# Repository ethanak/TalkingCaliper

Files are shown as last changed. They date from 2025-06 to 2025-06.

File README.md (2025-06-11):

# TalkingCaliper

A multilingual speaking caliper attachment.

## Short description

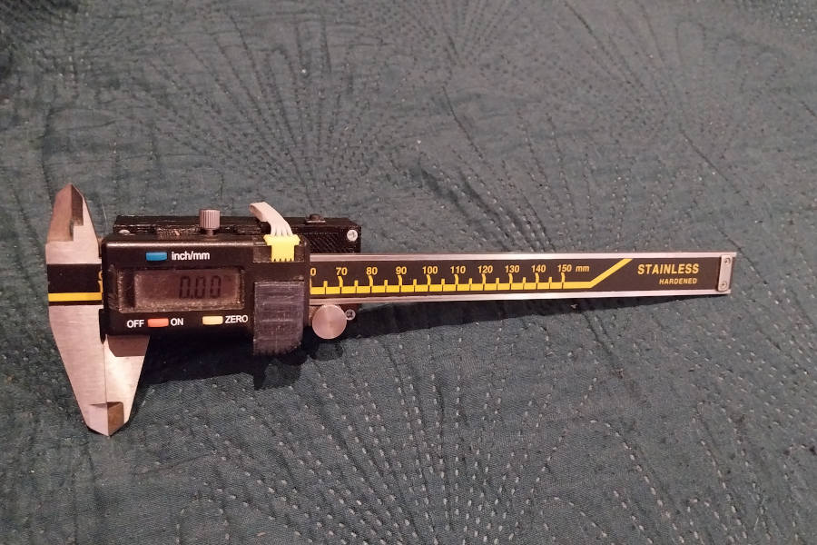
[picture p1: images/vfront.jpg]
general view


Short movie: [YouTube video](https://youtu.be/fLb1sWjNS7g)

The device is an attachment for the popular Vorel caliper, it can also be used in all measuring devices of this company with a compatible interface (tire tread depth gauge, dial gauge, etc.). In the case of the caliper, it is mounted on the rear wall of the housing in a way that does not interfere with its normal use.

The attachment allows for convenient use of the caliper;

* by blind and visually impaired people
* in poor lighting conditions
* in situations where observing the display is difficult or impossible

In contrast to previous designs using the full TTS mechanism (and thus limited to one specific language), a corpus synthesizer was used here. Due to the relatively small number of messages, it is possible to pre-record them in virtually any language. The program code allows you to select (during compilation) one of four languages:

* English (RHVoice, two voices bdl and slt);
* Polish (RHVoice, two voices magda and natan)
* Spanish (RHVoice, one voice mateo)
* German (Piper-TTS, one voice thorsten)

It is also possible to use an Android phone and use the phone's built-in TTS system, but it is not very convenient (especially for the first group of users)

The device can work in the following modes:

* continuous reading - current measurement results are provided with a one-second break
* reading changes - only measurement results are provided if the value has changed or a reading has been forced.
* reading on demand - after pressing a key.

The units (millimeters or inches) depend on the settings of the caliper itself. Each first reading ends with the unit being provided, the next ones are the same numbers. Since the result in millimeters always contains two decimal digits, in inches three, the reading is always unambiguous. Additionally, it is possible to set the reading option in thousandths of an inch for results below one inch (the unit is mil), in order to shorten the voice message without losing its intelligibility.

## Operation

The device has only one button. The options are as follows

* single click - in the change reading mode or on demand, it reads the current result;
* hold - changes the reading mode;
* double click - reads the battery status;
* click and hold - enters the settings mode.

In the settings mode:

* single click - change value
* hold - exit the settings mode without saving and return to the previous settings
* double click - change the parameter
* click and hold - save.

The following parameters can be set:

* speech speed (seven options, from absurdly slow to very fast);
* volume (three options);
* voice (only if there is more than one);
* way of reading small values;
* separation of digits when reading.

Additionally, after connecting the charger, the charging mode is started, where the device does not say anything. You can exit it by holding the key.

## Program

The program is currently only adapted to the XIAO ESP32S3 board.
Used in program:

* sonic_lite from library [Sonic](https://github.com/waywardgeek/sonic/)
* Piece of code for reading caliper data from  [EspDRO](https://github.com/MGX3D/EspDRO)

### Requirements:

* Arduino IDE with ESP32 Board version 3.1 or later installed
* ESP8266Audio library installed

### IDE settings:

- Selected board: XIAO ESP32-S3
- CPU Frequency: 80 MHz
- Partition Scheme: Maximum APP (7.9 MB APP, No OTA/No FS)

### Program settings:

In the common.h file:

```c
//Uncomment if you don't have/don't need the BlueTooth application
//#DISABLE_BLE

//Uncomment if you don't need charging control
//#DISABLE_CHARGER
```

In the i18n.h file:

```c

//Uncomment for language Polish
//#define VOICE_IS_PL
```

All other VOICE_IS definitions should be commented out.

For other languages:

* for English comment out all VOICE_IS definitions
* for others uncomment only the appropriate definition.

## Electronics

### Required elements

* XIAO ESP32-S3
* MAX98357A module
* Small speaker (originally used 15x24x4 1W)
* LiPo battery min. 250 mAh
* 2 x Schottky diode (min. 0.5A)
* 2 x rectifier diode (the smallest, any parameters) to power the caliper
* tact switch button
* small power switch
* resistors, capacitors, mounting elements according to the diagram

### Test version

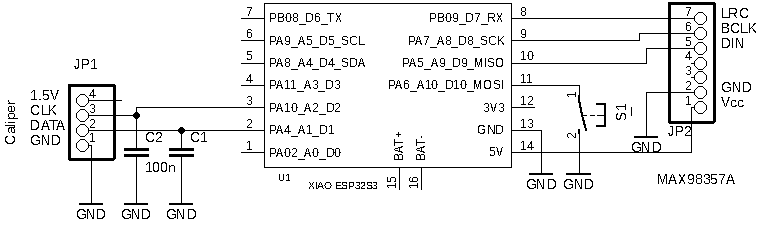
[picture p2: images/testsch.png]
simplified version diagram


This version is used only to test the program's cooperation with the caliper. It requires only three additional components beyond the main Xiao board and the amplifier (two capacitors and a button), but can be used both to evaluate the usability of the program and to work on introducing a new voice or language. The circuit can be assembled on a small (170 holes) breadboard.

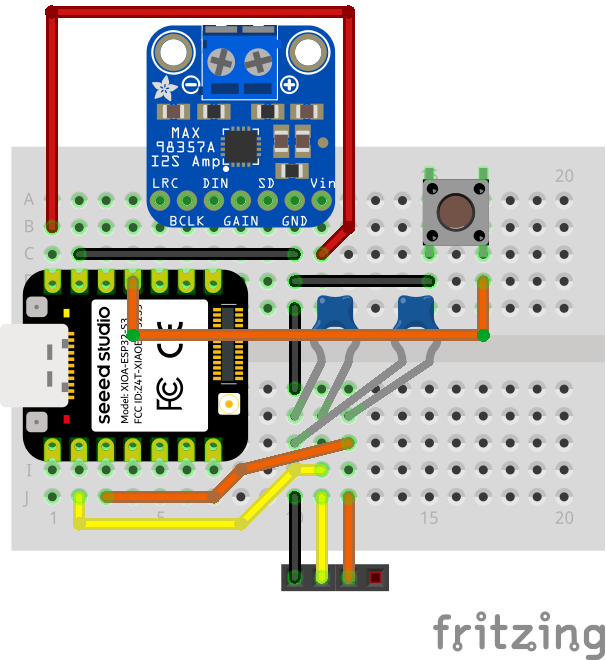
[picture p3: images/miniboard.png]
example breadboard layout


In this version, the caliper must be powered by an internal battery. When compiling, uncomment

```c
#DISABLE_CHARGER
```

in the common.h file so that the program does not try to check the charger connection to a non-existent battery.

Since there is no battery, the command to check the battery status will generate incorrect readings, but the rest will work.

### Base version

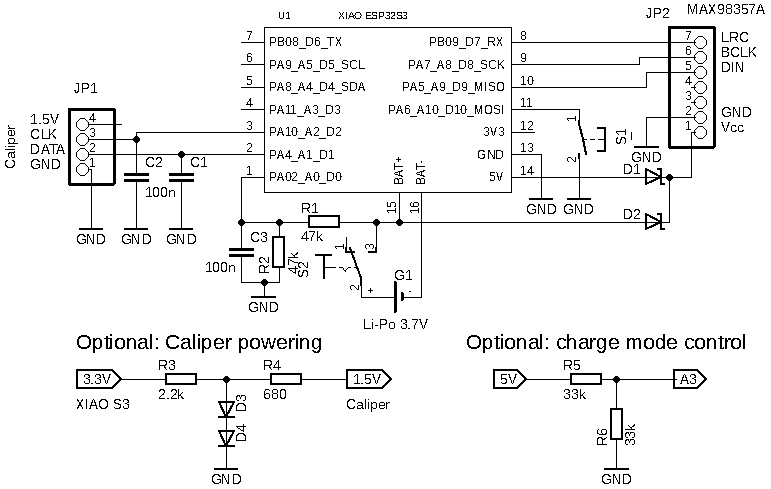
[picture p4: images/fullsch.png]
full version diagram


The simplest one that is realistically possible to make a working device. It differs from the previous one in that the amplifier power is taken either directly from the battery or (in the case of a USB connection) from the Vin input. Additionally, a battery status meter is already connected.

As before, the charger connection detection must be disabled.

Additional elements: two Schottky diodes, two resistors, optional capacitor.

Instead of Schottky diodes, you can use rectifier diodes of min. 0.5A as a last resort,
but you have to take into account that the voltage supplying the I2S amplifier circuit
may drop below the minimum required value of 2.5V with a partially discharged battery.

### Caliper power supply from the attachment battery

If the attachment is not permanently attached to the caliper, this should not be used and the caliper should be powered from the internal battery. In the case of a permanent connection, this should be considered: as a rule, the time needed to recharge the battery is at least an order of magnitude shorter than the time needed to find a battery store and buy one. And as we know, batteries discharge at the least expected moment... In addition, the system (including the caliper) can then be powered by any charger (if the battery is discharged).

Cost: two rectifier diodes, two resistors, connecting all four wires to the caliper plug. Additionally, approx. 1 mA of current draw from the battery.

It should be impossible to insert a battery into the caliper!

### Charging sensor

Allows the device to automatically switch to silent mode (it is not advisable for the device to talk during charging).

Cost: two resistors.

Comment required

```c
#DISABLE_CHARGER
```

in common.h file

### Notes

To calibrate the battery status sensor, access to gnd and the +bat pad is required. While this is trivial before installing the attachment (+bat is available on the switch leads, gnd in several places) - after installation, this is no longer possible. Remember this and calibrate before permanently installing the attachment.

## Mechanical design

### Caliper plug

The project is a modified version of the plug from [EspDRO](https://github.com/MGX3D/EspDRO).
You can also use the original version.

The plug should be printed from TPU or similar elastomer [STL file](/connector/mini_connector.jpg),
preferably with a 0.1 mm layer. The way to attach the cable is shown in the pictures in the [Connector](/connector/) folder.

### Housing

Due to the possibility of using different elements and configurations, it is not possible to include STL files. The attached file [OpenSCAD](/caliper.scad) can be a basis for designing the housing

## Other voices and languages.

It is possible to implement other voices (e.g. using commercial
synthesizers), as well as other languages. More information in the folder
[voice preparation](/prepare).

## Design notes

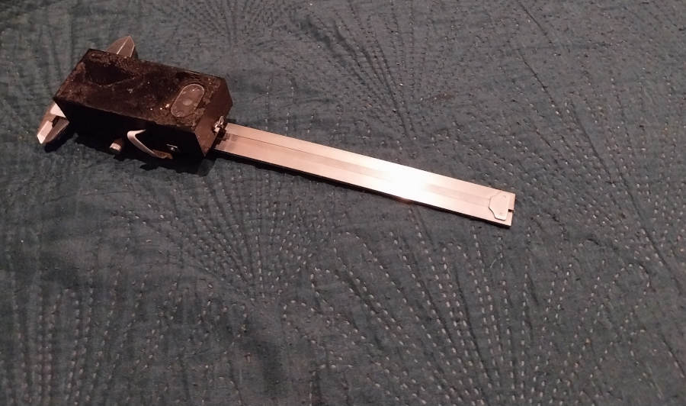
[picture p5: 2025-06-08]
images/vback.jpg

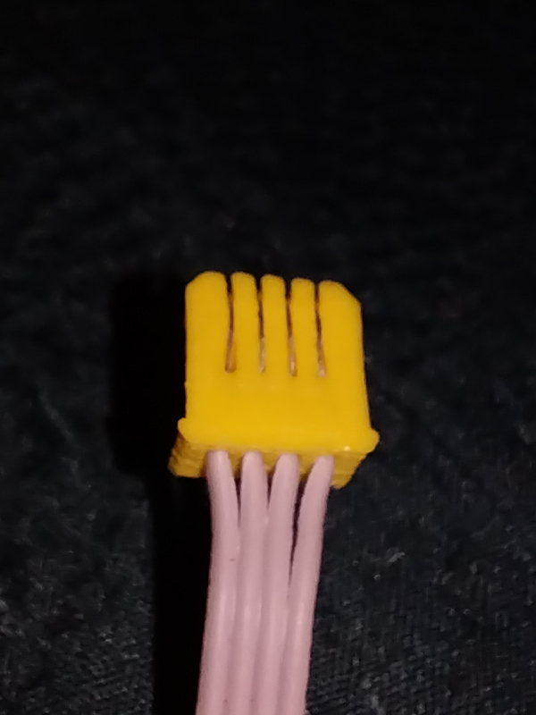
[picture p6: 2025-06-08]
connector/connb.jpg

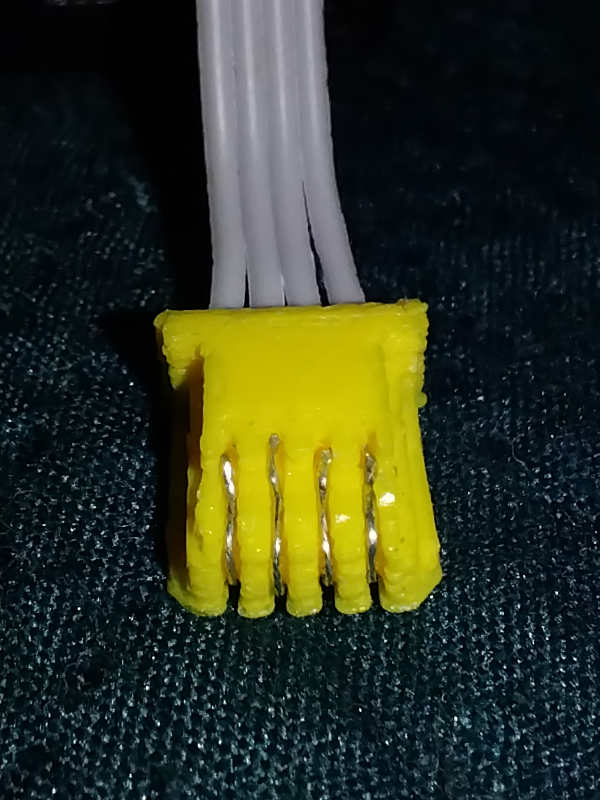
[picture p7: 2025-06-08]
connector/connf.jpg

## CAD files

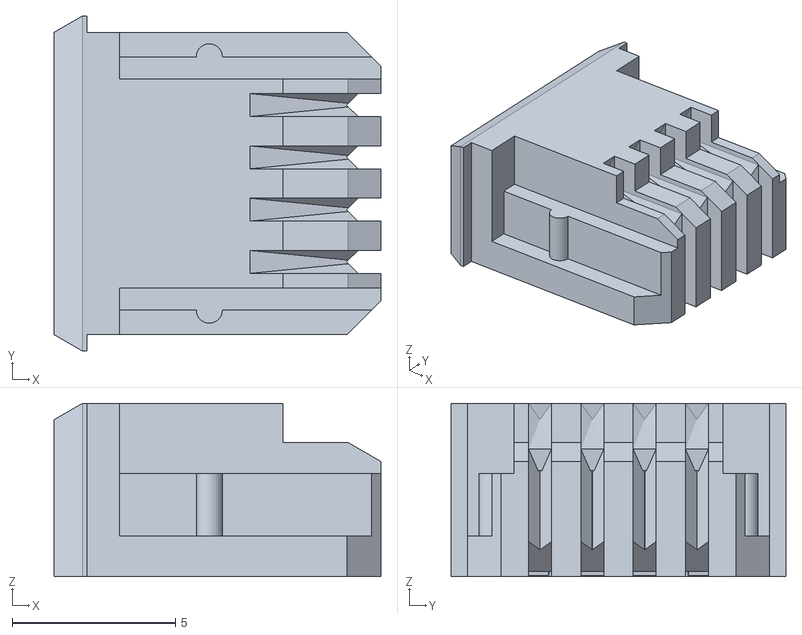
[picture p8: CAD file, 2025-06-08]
connector/mini_connector.stl
10.0 x 10.2 x 5.30

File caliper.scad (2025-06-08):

// what will be printed?
whatprint = 0; // [0:cover, 1: pokrywka, 2: speaker holder, 3: pcb holder]

module symetric(n=0)
{
    for (symetri3s = [0,1]) mirror([
        (n==0) ? symetri3s : 0,
        (n==1) ? symetri3s : 0,
        (n==2) ? symetri3s : 0]) children();
}
module icube(x,y,z)
{
    translate([-x/2, -y/2, 0]) cube([x,y,z]);
}

$fn=32;


// speaker dimensions
mi_d=15.8;
mi_l=24.8;
mi_h=4;
mi_left= mi_d/2+2;



wall = 1.6;
mainlen_ex = 75;
mainlen_in = mainlen_ex-2*wall;
mainwid_in = 30;
mainwid_ex=mainwid_in + 2*wall;
mainh_in = 17.4;
botom=2.1;
gtop=1.5;

// pcb holes
hdx=8*2.54;
hdy=10*2.54;
hlx=18.5+2*2.54;

pip1=[[12,24]];
pip2=[[12,12],[35,7]];

xkey=59;
wkey=6.4;
wswitch = 9.6;
piph=9;

module topik()
{
    translate([-wall,0,mainh_in+1]) difference()
    {
        union() {
            translate([0,-mainwid_ex/2,0]) cube([mainlen_ex,mainwid_ex,gtop]);
            translate([mainlen_in+wall,-wswitch/2+0.6,-2.4]) cube([wall,wswitch-1.2,2.5]);
            translate([pip2[1][0]+pip2[1][1]+0.4,mainwid_in/2,-6]) cube([7.2,wall,6.1]);
        }
        for (p=pip2) translate([p[0]-0.6,mainwid_in/2-1,-1]) cube([p[1]+1.2,5,5]);
        mirror([0,1,0]) translate([pip1[0][0]-0.6,mainwid_in/2-1,-1]) cube([pip1[0][1]+1.2,6,6]);
        for (x = [3, mainlen_ex-3]) symetric(1) {
            translate([x,mainwid_ex/2-3,-1]) {
                cylinder(d=2.4,h=10);
                translate([0,0,gtop-0.2]) cylinder(d1=2.5, d2=6.5, h=2);
            }
        }
    }
}
module spikiper()
{
    difference() {
        translate([-mi_left,-13.5,0]) cube([mi_left*2-2,27,1.3]);
        symetric(1) translate([mi_left-2-5,13.5-4,-1]) cube(6);
    symetric(1) translate([-mi_left+3,mainwid_in/2-3,-1]) cylinder(d=2.4,10);
        translate([0,0,-5]) hull() symetric(1) translate([0,(mi_l-mi_d)/2,0]) cylinder(d=mi_d-6,h=10);
    }
    icube(mi_left*2-5,6,0.9);
    cylinder(d=6,h=0.9+1.2);

}

module buda()
{
    module boks(h)
    {
        difference() {
            translate([-wall,-mainwid_ex/2,-botom]) cube([mainlen_ex,mainwid_ex,botom+h]);
            translate([0,-mainwid_in/2,0]) 
                cube([mainlen_in,mainwid_in, h+1]);
        }
    }
    
    module hole(ha)
    {
        hb=ha+2.1-0.9;
        cylinder(d=1.8,h=hb+1);
        cylinder(d=2.4,h=2);
        translate([0,0,hb-0.4]) cylinder(d1=1.8,d2=2.4,h=0.6);
    }
    
    difference() {
        union() {
            boks(mainh_in);
            // głośnik
            translate([mainlen_in-2*mi_left,-mainwid_in/2,-2.1+0.9]) cube([20.1,mainwid_in,1+mi_h]); 
            
            // dystans pod płytkę
            for (x=[hlx,hlx+hdx]) symetric(1) translate([x,hdy/2,-0.1]) {
                cylinder(d=4.5, h=2.1);
                translate([-4.5/2,0,0]) cube([4.5,3.5,2.1]);
            }
            // skrzydełka
            for (p=pip2) translate([p[0]-wall,mainwid_in/2,0]) cube([p[1],wall,mainh_in+piph]);
            for (p=pip1) translate([p[0]-wall,-mainwid_ex/2,0]) cube([p[1],wall,mainh_in+piph]);
             // mocowania topu prawe
            symetric(1) translate([mainlen_in+wall-6,mainwid_ex/2-6,mainh_in-5]) hull() {
                cube([5.5,5.5,5]);
                translate([5,5,-5]) cube(0.5);
            }
            // mocowania topu lewe
            symetric(1) translate([-wall,mainwid_ex/2-6,mainh_in-5]) hull() {
                cube([6,6,5]);
                translate([0,5,-5]) cube(0.5);
            }
            
            // klawisz
            translate([xkey-wkey/2-4.1,mainwid_in/2-3.6,mainh_in-wkey]) hull() {
                cube([wkey+8.2,4,wkey-1]);
                translate([4,4,-4]) cube([wkey+2,0.1,0.1]);
            }
            // wyłącznik
            *translate([-wall,-wswitch/2-4.1,mainh_in-6.8]) cube([wall+2+1.6,wswitch+8.4,6]);
            translate([mainlen_in-3.5,-wswitch/2-4.2,mainh_in-6.8]) {
                hull() {
                    cube([4,wswitch+8.4,6]);
                    translate([3.6,4,-4]) cube([0.4,wswitch+0.4,1]);
                }
            }
        }
        
        // śruby topu
        for (x = [3, mainlen_ex-3]) symetric(1) {
            translate([x-wall,mainwid_ex/2-3,mainh_in-6]) {
                cylinder(d=1.8,h=10);
                cylinder(d=2.4,h=3);
            }
        }
        // otwór na kabel
        translate([pip2[1][0]+pip2[1][1]-wall,mainwid_in/2-1,6]) cube([8,8,20]);
        // otwór na głośnik
        translate([mainlen_in-mi_left,0,-5]) hull() symetric(1) translate([0,(mi_l-mi_d)/2,0]) cylinder(d=mi_d-4,h=7);
        translate([mainlen_in-mi_left,0,-2.1+0.9]) hull() symetric(1) translate([0,(mi_l-mi_d)/2,0]) cylinder(d=mi_d+0.8,h=7);
        
        // otwory na mocowanie głośnika    
        translate([mainlen_in-mi_left,0,-2.1+0.9]) symetric(1) translate([-mi_left+3,mainwid_in/2-3]) hole(mi_h-2.1+0.9);
        // otwory na mocowanie płytki
        for (x=[hlx,hlx+hdx]) symetric(1) translate([x,hdy/2,-2.1+0.9]) hole(2);
        // usb
        translate([-wall-1,-6,4.4]) cube([wall+2,12,5]);
        // klawisz
        translate([xkey-wkey/2,mainwid_in/2-5,mainh_in-wkey]) cube([wkey,8,wkey+1]);
        translate([xkey-wkey/2-2.5,mainwid_in/2-2,mainh_in-wkey]) cube([wkey+5,2,wkey+1]);
        // wyłącznik
        *translate([-wall-1,-wswitch/2,mainh_in-6]) cube([wall+8,wswitch,7.5]);
        *translate([0,-wswitch/2-2.5,mainh_in-7]) cube([2,wswitch+5,8]);
        
        translate([mainlen_in-5,-wswitch/2,mainh_in-6]) cube([wall+8,wswitch,7.5]);
        translate([mainlen_in-2,-wswitch/2-2.5,mainh_in-7]) cube([2,wswitch+5,8]);
    }
}

hprz=5;
module przekladka()
{
    translate([0,0,0.9+hprz+3.6]) mirror([0,0,1]) difference()
    {
        union() {
            translate([20,-mainwid_in/2+1,0]) cube([hlx+hdx-16,mainwid_in -2, 0.9]);
            intersection() {
                for (x=[hlx,hlx+hdx]) symetric(1) translate([x,hdy/2,-0.1]) cylinder(d=4.5, h=0.9+hprz);
                translate([0,-mainwid_in/2+1,0]) cube([hlx+hdx+2,mainwid_in -2, 22.9]);
            }
        }
        translate([hdx+hlx-2.5,-10,-1]) cube([10,20,10]);
        symetric(1) translate([hlx+3,-mainwid_in/2,-1]) cube([hdx-8,6,4]);
        for (x=[hlx,hlx+hdx]) symetric(1) translate([x,hdy/2,-1]) {
            cylinder(d=2.4, h=9.1);
            cylinder(d1=6.4, d2=2.4,h=2);
        }
        // really?
        translate([0,-mainwid_in/2,-1]) cube([hdx+8,6,24]);
    }
}

if (whatprint == 0) buda();
else if (whatprint == 1) topik();
else if (whatprint == 3) przekladka();
else if (whatprint == 2) spikiper();

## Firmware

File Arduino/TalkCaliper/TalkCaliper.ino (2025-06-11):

/*
   Copyright 2025 Bohdan R, Rau <ethanak@polip.com>

   Licensed under the Apache License, Version 2.0 (the "License");
   you may not use this file except in compliance with the License.
   You may obtain a copy of the License at

     http://www.apache.org/licenses/LICENSE-2.0

   Unless required by applicable law or agreed to in writing, software
   distributed under the License is distributed on an "AS IS" BASIS,
   WITHOUT WARRANTIES OR CONDITIONS OF ANY KIND, either express or implied.
   See the License for the specific language governing permissions and
   limitations under the License.
*/
#ifndef DISABLE_BLE
#include <WiFi.h>
#endif
#include <stdarg.h>
#include <driver/adc.h>
#include <esp_adc_cal.h>
#include "i18nstrings.h"
#include VOXDEFS
#include "common.h"
//#include "soc/rtc_wdt.h"

esp_adc_cal_characteristics_t db11_chars;


uint8_t lastInch=0xff;
uint32_t lastRead;
uint32_t lastSpoken;
uint8_t mainSpeed=0;
uint8_t mainVox=0;
uint8_t mainVol=0;
uint8_t lpfilter = 0;
static bool chargeMode, lastChargeMode;
static uint8_t chargeCnt;
static uint32_t lastChargeTimer = 0;
uint16_t calibV1, calibV2;
#ifndef DISABLE_BLE
char blename[32];
bool autoBLE;
#endif

enum {
    RDM_STILL = 0,
    RDM_CHAN,
    RDM_REQ,
    RDM_CHARGE,
    RDM_MAX
};

enum {
    MAMO_STD = 0,
    MAMO_PFS
};

#ifdef MOVIE_MODE
enum {
#if VOICE_COUNT > 1
    PFMO_VOX = 0,
#endif
    PFMO_OVER,
    PFMO_TEMPO,
    PFMO_VOL,
    PFMO_MILS,
#ifndef DISABLE_MELODY
    PFMO_MELO,
#endif
    PFMO_MAX
};

#else
enum {
    PFMO_TEMPO = 0,
    PFMO_VOL,
#if VOICE_COUNT > 1
    PFMO_VOX,
#endif
    PFMO_MILS,
#ifndef DISABLE_MELODY
    PFMO_MELO,
#endif
    PFMO_OVER,
    PFMO_MAX
};

#endif


const uint8_t readModeSpk[] = {
    vword_xsstil,
    vword_xschan,
    vword_xsrequ,
    vword_xcharge
};

const char * const readModeTxt[] = {
    STR_RDSTIL,
    STR_RDCHAN,
    STR_RDREQU,
    STR_RDCHRG
};

int wordBuffer[32],wordBufLen;
char blubuffer[256];
uint8_t readMode = RDM_STILL;
uint8_t mainMode = MAMO_STD;
uint8_t pfsMode = 0;
bool enableMelody, disablePauses, enableMils;
static bool tmpMelody, tmpPauses, tmpMils;


extern void speakLocal(int cnt, const char *txt=NULL);

#if defined(DISABLE_CHARGER)
#define chargerConnected 0
#else

#ifdef DIGITAL_VIN_PIN
#define chargerConnected digitalRead(VIN_PIN)
#else
#define chargerConnected (adc1_get_raw(VIN_CHANNEL) > 500)
#endif

#endif

void setup(void)
{
    Serial.begin(115200);
    setCpuFrequencyMhz(80);

#ifndef DISABLE_BLE
    WiFi.mode(WIFI_MODE_NULL);
#endif
    adc1_config_width(ADC_WIDTH_BIT_12);
#ifdef DIGITAL_VIN_PIN
    pinMode(VIN_PIN,INPUT);
#else
    adc1_config_channel_atten(VIN_CHANNEL,ADC_ATTEN_DB_11);
#endif
    adc1_config_channel_atten(VOLT_CHANNEL,ADC_ATTEN_DB_11);
    adc1_config_channel_atten(CLK_CHANNEL,ADC_ATTEN_DB_6);
    adc1_config_channel_atten(DATA_CHANNEL,ADC_ATTEN_DB_6);
    esp_adc_cal_characterize(
        ADC_UNIT_1, ADC_ATTEN_DB_11, ADC_WIDTH_BIT_12,
        1100, &db11_chars);
    initPrefs();
    revertPrefs();
    //getCalibData();
    pinMode(KEY_PIN, INPUT_PULLUP);
#ifndef DISABLE_BLE
    delay(100);
    if (autoBLE) useBLE = true;
    else if (!digitalRead(KEY_PIN)) {
        delay(100);
        if (!digitalRead(KEY_PIN)) useBLE=true;
    }
#endif
    startSecondTask();
    delay(10);
    chargeMode = chargerConnected;
    readMode=(chargeMode) ? RDM_CHARGE : RDM_STILL;
    chargeCnt = 0;
    
    //initKey();
#ifndef DISABLE_BLE
    if (useBLE) {
        wordBuffer[0] = vword_xblu;
        wordBuffer[1] = readModeSpk[readMode];
        speakLocal(2);
    }
    else
#endif
     {
        wordBuffer[0] = readModeSpk[readMode];
        speakLocal(1);
    }
    lastChargeMode = chargeMode;
    lastRead=millis();
    lastChargeTimer = millis();
}

static uint32_t _readBattery()
{
    static uint32_t batsum=0;
    static uint8_t batstep=0;
    static uint32_t batmillis = 0;
    uint32_t curvolt;
    if (millis() - batmillis < 50) return 0;
    batmillis = millis();
    if (esp_adc_cal_get_voltage(ADC_CHANNEL_0,&db11_chars,&curvolt) != ESP_OK) return 0;
    if (batstep == 0) batsum = 0;
    batsum += curvolt;
    batstep = (batstep + 1) & 15;
    if (batstep == 0) return batsum / 16;
    return 0;
    
}

int batvolt = 0;

void readBattery()
{
    int t = _readBattery();
    if (t) batvolt = t;
}

void getStrResult(char *buf, long packet)
{
    static const char *units[]={
        " mm"," in"," ms"};
        
    long data = packet & 0xFFFFF;
    char *cb=buf;
    uint8_t neg = (packet & 0x100000) ? 1 : 0;
    uint8_t inch;
    if (packet & 0x800000) {
        data = data/2;
        inch = (enableMils && data < 1000) ? 2: 1;
        
    }
    else inch=0;
    if (neg) {
        strcpy(buf,"- ");
        buf+=2;
    }
    if (inch == 2) sprintf(buf,"%d ms", data);
    else {
        if (inch) sprintf(buf,"%d . %03d", data/1000, data%1000);
        else sprintf(buf,"%d . %02d", data/100, data%100);
        if (lastInch != inch) {
            strcat(buf, units[inch]);
        }
    }
    lastInch = inch;
}


uint32_t pfsTimer;
uint8_t tmpSpeed, tmpVox, tmpVol;
bool speaking = false;
void speakLocal(int cnt, const char *txt)
{
    qSay(mainVox, mainSpeed, mainVol, cnt, wordBuffer,txt);
    speaking = true;
}

static void vspeakTmp(int cnt, ...)
{
    int i;
    va_list ap;
    va_start(ap, cnt);
    for (i=0;i<cnt;i++) wordBuffer[i] = va_arg(ap, int);
    va_end(ap);
    qSay(tmpVox, tmpSpeed, tmpVol, cnt, wordBuffer);
    speaking = true;
}    

void announceRDM(void)
{
    wordBuffer[0] = readModeSpk[readMode];
    speakLocal(1,readModeTxt[readMode]);
}

void announcePfs(void)
{
    switch (pfsMode) {
        case PFMO_TEMPO:
        vspeakTmp(2, vword_xspeedp, (tmpSpeed+1) * NUMSTEP);
        break;

        case PFMO_VOL:
        vspeakTmp(1, vword_xvol0+tmpVol);
        break;

#if VOICE_COUNT > 1
        case PFMO_VOX:
        vspeakTmp(2,vword_xvtypp,vword_xvox);
        break;
#endif

        case PFMO_MILS:
        vspeakTmp(1, enableMils? vword_xmilson : vword_xmilsof);
        break;
        
        case PFMO_OVER:
        vspeakTmp(1, disablePauses? vword_xoveron : vword_xoverof);
        break;

#ifndef DISABLE_MELODY
        case PFMO_MELO:
        vspeakTmp(1, enableMelody ? vword_xmelon : vword_xmelof);
        break;
#endif
    }
}


void startMamoPfs(void)
{
    mainMode = MAMO_PFS;
    pfsMode = 0;
    tmpSpeed = mainSpeed;
    tmpVox = mainVox;
    tmpVol = mainVol;
    announcePfs();
    pfsTimer = millis();
    
}

void doMamoPfs(uint8_t cmd)
{
    if ((!cmd && (millis() - pfsTimer > 10000)) || cmd == KCMD_LONG) {
        mainMode = MAMO_STD;
#ifndef DISABLE_MELODY
        enableMelody = tmpMelody;
#endif
        disablePauses = tmpPauses;
        enableMils = tmpMils;
        wordBuffer[0] = vword_xcancel;
        speakLocal(1);
        return;
    }
    pfsTimer = millis();
    switch(cmd) {
        case KCMD_DBLE:
        pfsMode = (pfsMode + 1) % PFMO_MAX;
        announcePfs();
        return;
    
        case KCMD_DLONG:
        mainSpeed = tmpSpeed;
        mainVox = tmpVox;
        mainVol = tmpVol;
        storePrefs();
        mainMode = MAMO_STD;
        wordBuffer[0] = vword_xstored;
        speakLocal(1);
        
        //announceRDM();
        return;
        
        case KCMD_SGL:
        switch (pfsMode) {

#if VOICE_COUNT > 1
            case PFMO_VOX:
            tmpVox = (tmpVox+1) % VOICE_COUNT;
            break;
#endif
            case PFMO_VOL:
            tmpVol = (tmpVol+1) % 3;
            break;

            case PFMO_TEMPO:
            tmpSpeed = (tmpSpeed + 1) % 7;
            break;

#ifndef DISABLE_MELODY
            case PFMO_MELO:
            enableMelody = !enableMelody;
            break;
#endif
            case PFMO_MILS:
            enableMils = !enableMils;
            break;

            case PFMO_OVER:
            disablePauses = !disablePauses;
            break;
        }
        announcePfs();
        return;
    }
}

int lastSaidPacket=-1;
int lastKnownPacketValue = PACKET_NO_DATA;
int lastSpokenValue = PACKET_NO_DATA;

void sayPacket(int packet)
{
    char buf[32];
    getStrResult(buf, packet);
    lastSaidPacket=packet;
    lastSpokenValue = lastKnownPacketValue = packetValue(packet);
    mdits(buf);
    qSay(mainVox, mainSpeed,mainVol,  wordBufLen, wordBuffer,blubuffer);
    speaking = true;
}

static void spkOff()
{
    if (millis() - lastSpoken > 20000) {
        wordBuffer[0] = vword_xvoff;
        speakLocal(1);
    }
}

void spkBattery(void) {
    int level = batPercent((batvolt * calibV1) / calibV2);
    makebat(level);
    speakLocal(wordBufLen, blubuffer);
}

#ifndef DISABLE_CHARGER
void chargeCtl(void)
{
    if (millis() - lastChargeTimer < 100) return;
    lastChargeTimer = millis();
    bool cm = chargerConnected;
    if (cm != lastChargeMode) {
        chargeCnt = 0;
        lastChargeMode = cm;
        return;
    }
    if (chargeMode == cm) return;
    chargeCnt++;
    if (chargeCnt < 3) return;
    chargeMode = lastChargeMode = cm;
    if (!chargeMode) {
        if (readMode != RDM_CHARGE) return;
        readMode = RDM_STILL;        
    }
    else {
        if (readMode == RDM_CHARGE) return;
        readMode = RDM_CHARGE;
    }
    announceRDM();
}
#endif
bool canSayChange(long packet)
{
    if (lastKnownPacketValue == PACKET_NO_DATA) return true;
    int pv=packetValue(packet);
    if (abs(lastKnownPacketValue - pv) > 10) {
        lastKnownPacketValue = pv;
        return false;
    }
    if (abs(lastSpokenValue - pv) < 2) return false;
    return true;
}

static void avoidUglyMessage(void)
{
    static uint32_t ds=millis();
    static uint8_t md = 2;
    if (!md) return;
    if (millis() - ds >= 1000) {
        printf("\n"); md--;ds=millis();
    }
}


void loop()
{
    avoidUglyMessage();
    serLoop();
    readBattery();
#ifndef DISABLE_CHARGER
    chargeCtl();
#endif
    uint8_t cmd=getCmd();
    if (cmd) {
        qSay(0,0,0,0,NULL);
        qSay(0,0,0,0,NULL);
        lastSpoken = millis();
    }

    if (speaking && !isSpeaking()) {
        speaking = false;
        lastSpoken = millis();
    }
        
    if (mainMode == MAMO_PFS) {
        doMamoPfs(cmd);
        return;
    }
    if (cmd == KCMD_DBLE) {
        spkBattery();
        return;
    }
    if (cmd == KCMD_DLONG) {
        startMamoPfs();
        return;
    }
    
    if (cmd == KCMD_LONG) {
#ifdef DISABLE_CHARGER
        readMode = (readMode + 1) % RDM_MAX;
#else
        readMode = (readMode + 1) % (chargeMode ? RDM_MAX : RDM_CHARGE);
#endif
        announceRDM();
        return;
    }

    if (readMode == RDM_CHARGE) return;
    
    int packet=getPacket();
    if (packet >= 0) {
        lastRead = millis();
        if (!speaking) switch(readMode) {
            case RDM_CHAN:
            if (cmd == KCMD_SGL || (millis() - lastSpoken >= 1000 && lastSaidPacket != packet && canSayChange(packet))) sayPacket(packet);
            else spkOff();
            break;

            case RDM_REQ:
            if (cmd == KCMD_SGL) sayPacket(packet);
            else spkOff();
            break;

            default:
            if (millis() - lastSpoken >= 1000) {
                sayPacket(packet);
            }
            break;
        }
    }
    else if (!speaking) {
        if (millis() - lastRead > 10000) {
            lastSaidPacket = -1;
            wordBuffer[0] = vword_xnosig;
            lastRead=millis();
            speakLocal(1,STR_NOSIG);
        }
        else spkOff();
    }
    lastKnownPacketValue = packetValue(packet);
    
}

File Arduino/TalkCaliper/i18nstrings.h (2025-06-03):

/*
   Copyright 2025 Bohdan R, Rau <ethanak@polip.com>

   Licensed under the Apache License, Version 2.0 (the "License");
   you may not use this file except in compliance with the License.
   You may obtain a copy of the License at

     http://www.apache.org/licenses/LICENSE-2.0

   Unless required by applicable law or agreed to in writing, software
   distributed under the License is distributed on an "AS IS" BASIS,
   WITHOUT WARRANTIES OR CONDITIONS OF ANY KIND, either express or implied.
   See the License for the specific language governing permissions and
   limitations under the License.
*/

#ifndef I18NSTRINGS_H
#define I18NSTRINGS_H

#include "i18n.h"

#if defined(VOICE_IS_PL)

// numbers
#define STR_ZERO "zero"
#define STR_MINUS "minus"
#define STR_MILS "mils"
#define STR_MM "milimetra"
#define STR_INCH "cala"
#define STR_IDOT "i"

#define STR_INTRANGE "Podaj liczbę z zakresu %d..%d\n"
#define STR_UNFIN "Nie ukończono pomiaru, spróbuj za chwilę\n"
#define STR_SAVED "Zapisane\n"
#define STR_BALWAYS "zawsze"
#define STR_BDEMAND "na żądanie"
#define STR_FLTR "Filtr: %s\n"
#define STR_FLTR0 "wyłączony"
#define STR_FLTR1 "słaby"
#define STR_FLTR2 "średni"
#define STR_FLTR3 "silny"
#define STR_Y 't'
#define STR_N 'n'
#define STR_YORN "Podaj 't' albo 'n'\n"
#define STR_PFLONG "Czas długiego wciśnięcia %d msec\n"
#define STR_PFDBLE "Odstęp drugiego wciśnięcia %d msec\n"
#define STR_HCAL "Kalibracja"
#define STR_HBLE "Włączenie BLE"
#define STR_HLNG "Czas długigo wciśnięcia"
#define STR_HDBL "Odstęp podwójnego kliknięcia"
#define STR_HHLP "Pomoc"
#define STR_HLCAL "Podaj aktualną wartość napięcia w mV"
#define STR_HLBLE "Wpisz t jeśli BLE ma być zawsze włączony, n jeśli nie"
#define STR_HLLNG "Podaj czas długiego wciśnięcia w msec (300..600)"
#define STR_HLDBL "Podaj odstęp dla podwójnego przyciśnięcia w msec (200..600)"
#define STR_HLHLP "Z parametrem: pomoc dla konkretnego polecenia"
#define STR_HFLT "Filtr dolnoprzepustowy"
#define STR_HLFLT "Podaj moc filtra 0 to 3"
#define STR_HSTR1 "Polecenie bez parametrów podaje aktualne wartości\n"
#define STR_HSTR2 "Wpisz \"help polecenie\" aby uzyskać pomoc dla polecenia\n"
#define STR_HBNAME "Nazwa BLE"
#define STR_HLBNAME "Podaj nazwę pod którą będzie widziane urządzenie"   
#define STR_CURBLE "Aktualna nazwa: %s\n"
#define STR_BADNAME "Błędna nazwa\n"

#define STR_RDSTIL "odczyt ciągły"
#define STR_RDCHAN "odczyt zmian"
#define STR_RDREQU "odczyt na żądanie"
#define STR_RDCHRG "tryb ładowania"
#define STR_NOSIG "brak odczytu"
#define STR_BATTERY "Bateria: %d procent"

//misc
#define STR_BLELANG "*pl\n"

// spanish here
#elif defined VOICE_IS_ES

//numbers - wymawiane przez apkę na komórce
#define STR_ZERO "cero"
#define STR_MINUS "menos"
// jednosylabovy - ma być krótko, a elektronik to zrozumie
// milésimas de pulgada, a nawet samo milésimas jest za długie
#define STR_MILS "mils"
#define STR_MM "milimetros"
#define STR_INCH "pulgadas"
#define STR_IDOT "punto"

// todo: translate into Spanish

#define STR_INTRANGE "Introduzca un número entre %d y %d\n"
#define STR_UNFIN "Medición no completada, inténtelo de nuevo\n"
#define STR_SAVED "Guardado\n"
#define STR_BALWAYS "siempre"
#define STR_BDEMAND "a pedido"
#define STR_FLTR "Low pass filter: %s\n"
#define STR_FLTR0 "off"
#define STR_FLTR1 "weak"
#define STR_FLTR2 "medium"
#define STR_FLTR3 "strong"
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
